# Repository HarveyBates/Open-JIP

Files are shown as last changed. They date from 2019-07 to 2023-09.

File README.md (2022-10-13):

<p align="center">
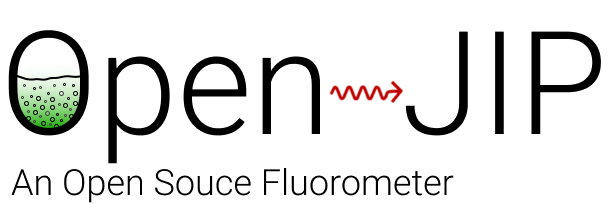
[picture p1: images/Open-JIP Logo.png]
  
</p>

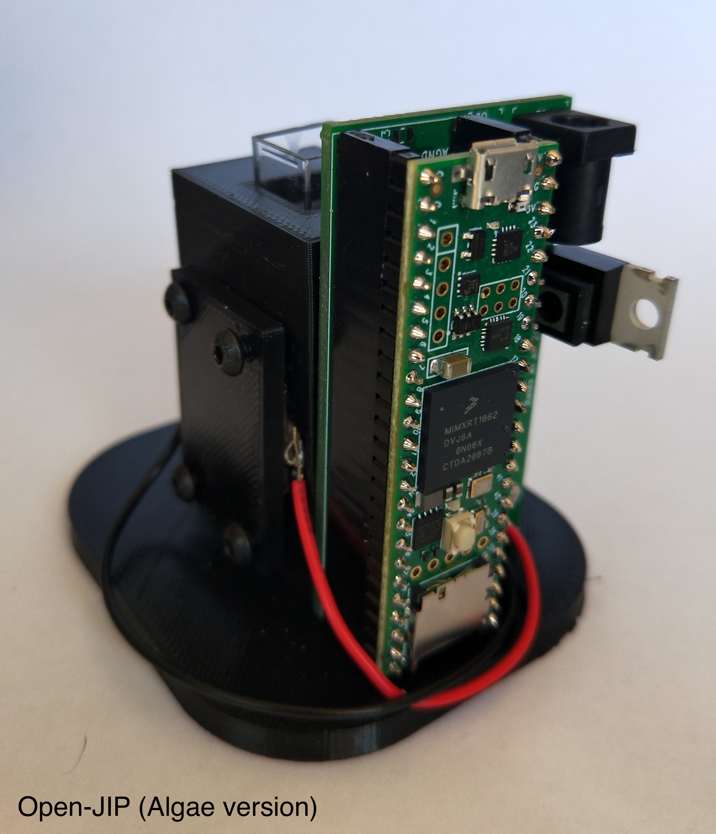
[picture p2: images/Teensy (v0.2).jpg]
### Description

Open-JIP is an open-source chlorophyll *a* fluorometer used to quantify photosynthetic phenotypes in terrestrial plants and microalgae. It is controlled via a Teensy microcontroller and features highly customisable electrical components and a 3D-printed infrastructure. 

#### OJIP

Open-JIP utilises a technique known as the fast polyphasic rise fluorescence
(also known as OJIP). Steady irradiance is provided from an emitting LED, this
excites photosynthetic antenna in the sample resulting in excess irradiance
being emitted as photons of a longer wavelength (i.e. fluorescence). The
emitted fluorescence, which contains information regarding the state of
photosynthesis, is captured by a photodiode, amplified by the custom circuitry
and stored by the Teensy microcontroller. This all happens in less than a second.

The transient captured by Open-JIP gives the user an indication of the state of photosynthesis in the subject organism to varying levels of complexity. If you would like to know more about the theory surrounding the measurement of chlorophyll *a* fluorescence, this [link](https://doi.org/10.1016/j.algal.2020.102105) gives a basic introduction and resources for further reading.

### Publication

The original device which used an Arduino Mega was published in [Photosynthesis Research in 2019](https://doi.org/10.1007/s11120-019-00673-2):

*A guide to Open-JIP, a low-cost open-source chlorophyll fluorometer - Bates et al. 2019*

If you would like to see what the device is capable of, you may be interested in this recent [publication](https://doi.org/10.1016/j.algal.2020.102105) which uses Open-JIP as a flow-through chlorophyll *a* fluorometer connected [a custom photobioreactor](https://github.com/HarveyBates/Phenobottle) with the microalga *Chlorella vulgaris*.

### Collaborations and custom architecture 

If you would like to collaborate on a project, or would like to see if Open-JIP can be customised to suit your application, please email me at [harvey_bates@hotmail.com](mailto:harvey_bates@hotmail.com). 

### Disclaimer

Open-JIP requires some knowledge of electronics, programming and photosynthesis to operate. If you have problems with the device place an issue in the [issues](https://github.com/HarveyBates/Open-JIP/issues) tab of this repository and I will do my best to address it as soon as possible.

# USER MANUAL

Below contains the user manual for Open-JIP, if you have any questions there is a discussions tab in this github repository, where I will do my best to get back to you as soon as possible.

## Contents

1. Introduction
   1. Specifications
   2. Getting started
      1. Downloading files
         1. Method 1 (New users)
         2. Method 2 (Experienced users / collaborators)
      2. Gathering materials
         1. Printed circuit board (PCB)
            1. Ordering a PCB
         2. 3D models
         3. Additonal parts
2. Firmware / Software
   1. Introduction
   2. Arduino IDE / Teensyduino
   3. Basic operations
      1. Basic functions
      2. Advanced functions
      3. Calibration functions
   4. Python control
   5. Advanced operations
      1. Change actinic LED intensity
      2. Change detection sensitivity
      3. Set analog reference voltage & Resolution
      4. Defaults
      5. Length of actinic pulse
3. Hardware
   1. Detection
      1. Gain adjustment 
   2. Actinic Intensity

## 1. Introduction

### Specifications

| Feature            | Value / Description                                          |
| ------------------ | ------------------------------------------------------------ |
| Actinic LED Colors | **Blue** 455 – 485 nm (466 nm), **Green** 517 – 555 nm (532 nm), **Orange** 583 – 600 nm (593 nm), **Red** 617 – 635 nm (626 nm). |
| Resolution         | 10 to 16-bit (optimised for 12-bit)                          |
| Sampling rate      | 8 &mu;s at 12-bits                                           |
| Operating voltage  | 15 V 1.2 A (Barrel plug)                                     |
| Communications     | USB (Serial)                                                 |
| Microcontroller    | Teensy 3.5/3.6 or Teensy 4.1 (3.6 Recommended)               |
| Actinic Intensity  | Four intensities (Low, Mid, High, Very High)                 |
| Detection (Gain)   | Four settings (Low, Mid, High, Very High)                    |

### Getting started

#### Downloading files

##### Method 1 (New users)

New users should navigate to the [releases](https://github.com/HarveyBates/Open-JIP/releases) page to find the most recent (and stable) version of the device. You can download the latest release as a `.zip` file and this will contain all the files you need to get the device up and running. 

The most recent version is **v0.3**. 

When searching through files in this repository all relevant folders are labeled with a specific version. You will want to use files that match the version you are using.

##### Method 2 (Experienced users / collaborators)

If you want to contribute to the project or fork this directory feel free to do so, just know that I constantly update files here so they may not function as expected before release. 

To clone this directory type this into your terminal / console.

```bash
git clone https://github.com/HarveyBates/Open-JIP.git
```

#### Gathering materials

Open-JIP can be built in an afternoon if you have all the equipment at hand. The folder "Bill of Materials" contains all the materials needed to build Open-JIP. This has been divided into two parts; (1) circuit board and (2) other. 

In addition to the Bill of Materials you will need to have access to:

1. A soldering iron
2. Solder (Paste or wire variety)
3. A re-flow oven (not necessary but makes the circuit board easier to assemble)
4. A 3D-printer
5. A pair of wire strippers / cutters
6. Some tweezers

##### Printed circuit board (PCB)

In the ```Bill of Materials/Circuit Board``` folder you will find a table all the components needed to construct the Open-JIP circuit board. These components can be bought from common electronics suppliers such as [digikey](https://www.digikey.com/), [LCSC](https://lcsc.com/en) or [farnell](https://au.element14.com/) etc. Links for each component is provided.

Note that most of the components are surface mount (SMD), this is due to their increased reliability and in my opinion its easier to assemble SMD compared to through-hole (THT) components. 

###### Ordering a PCB

To order the circuit board I recommend using [JLCPCB](https://jlcpcb.com/) as they are cheap, easy and ship fast. 

1. Open the folder titled Electronics 
2. Navigate to your current version 
3. In the subdirectory select the folder containing gerber and drl files
4. Compress this folder into a ```.zip``` file. 
5. On the JLCPCB website drag and drop the ```.zip``` file into the order form. 

The default settings are suitable. 

##### 3D Models

The 3D-models used for 3D-printing Open-JIP can be found in the ```Open-JIP/Hardware``` folder. Two file types are specified:

1. ```.stl``` can be directly imported into 3D-printing software such as [Ultimaker-Cura](https://ultimaker.com/software/ultimaker-cura) or sent to a local 3D-printing manufacturer.
2. ```.STEP``` is the modifiable Open-JIP 3D-model and as such can be configured whichever way you want before being exported as a ```.stl``` file. You can use 3D modeling software to do this such as [Fusion360](https://www.autodesk.com/products/fusion-360/overview) or [Solidworks](https://www.solidworks.com/).

##### Additional parts

In addition to the above electronics you will need a few components such as a Teensy microcontroller, power supply, computer to use the device etc. A table of all these additional items can be found in the folder location ```Bill of Materials/Other```.

## 2. Firmware / Software

### Introduction

Open-JIP operates via a computers serial port (USB connection), the user sends commands in the form of strings that are read by the Teensy microcontroller. This results in the device taking a measurement or other tasks. You can do this manually though the Arduino IDE or by using scripts in various languages. 

### Arduino IDE / Teensyduino

To setup the Teensy (upload the firmware to the microcontroller) you will need **both** [Arduino IDE](https://www.arduino.cc/en/software) and [TeensyDuino](https://www.pjrc.com/teensy/teensyduino.html) if running on Linux or Windows, or just [TeensyDuino](https://www.pjrc.com/teensy/teensyduino.html) if using a Mac. Instructions on how to do this is provided in the above links. 

When first using Open-JIP: 

1. Plug the Teensy into your computer
2. Open Arduino IDE
3. Select ```Tools>Board>Teensy 3.6``` (may be in another part called Teensyduino)
4. Select ```Port>"Your Teensy Device"```
5. ```File>Open``` the "Teensy.ino" file found in ```Firmware/v0.3/Teensy_3.6/Teensy_3.6.ino```
6. ```Sketch>Upload``` to flash the file onto the Teensy

The provided ```Teensy.ino``` file will work as is, but if you wish to change settings in this file you will need to reupload the firmware to the Teensy again after changes have been made.

### Basic Operations

To take a measurement open the serial monitor (in the Arduino IDE when the device is connected to your computer) (```Tools>Serial Monitor```) and type in the command ```MF``` (denoting **m**easure **f**luorescence). This will (in the default configuration) take a one second measurement of chlorophyll *a* fluorescence and print the resulting measurements out into the serial monitor. You can copy and paste the data into excel in order to graph the transient.

There are a number of included functions that require the same method to operate:

#### Basic functions

1. ```MF``` - **M**easure fluorescence. Measure the chlorophyll *a* fluorescence signature of the organism of interest. 
2. ```CP``` - **C**alculate **p**arameters. Calculate and print out basic fluorescence parameters from the most recent OJIP curve. 
3. ```CFo``` - **C**alibrate **F<sub>o</sub>** (the minimum level fluoresence). Provides short flashes of illumination for calibrating the minimum level fluorescence. This command is useful if you want to know if your measurement is going to *saturate* (due to an overly concentrated sample) before taking a measurement. 
4. ```An``` - **A**ctinic intensity (irradiance of LED) where *n* is a number between 1 and 4 (lowest to highest).
5. ```Fn``` - **F**luorescence gain (sensitivity of detection) where *n* is a number between 1 and 4 (lowest to highest).

**Note** - It is recommended that the minimum level of fluorescence (F<sub>o</sub>) is greater than 0.3 V for the maximum stability of acquisitions.

#### Advanced functions

1. ```MJ``` - **M**easure **J**-step. Measures up to the J-step (~2 ms) and returns the data to the serial port.
2. ```MW``` - **M**easure **w**ave. Measures up to the J-step multiple times with set time intervals between acquisitions. 

#### Calibration functions

1. ```ML``` - Calibrate actinic intensity (**m**easure **l**ight). Turns on the actinic LED for a period of three seconds to allow the intensity to be measured by a 4&#960; light meter.
2. ```Cr``` **C**alibrate **r**ise time of the actinic LED/amplifier combination. Provides some short  (100us) flashes of illumination from the actinic LED to calibrate your setup using an external oscilloscope. Useful if you want to ensure your Fo value is accurate (i.e. Fo should be measured when the actinic LED and amplifier are stable (usually around 40us)). *Note* this is only nessesary if you alter the default electronics configuration (see below).  

### Python Control

Open-JIP comes with an external cross platform python script that allows users to take basic measurements, plot the data and sort it into a ```.csv``` file automatically. This program is located under ```External Control/Open-JIP.py```.

```Open-JIP.py``` uses [plotly](https://plotly.com/python/) to plot the data and [pyserial](https://pyserial.readthedocs.io/en/latest/pyserial.html) to access the serial port of your machine. You must have [python](https://www.python.org/) installed to use this script. **This program runs in the terminal / console**. Additonally you need pip to install these requirements as follows:

```bash
cd Open-JIP/Software
pip3 install -r requirements.txt
python3 Open-JIP.py
# or (depending on python installation)
pip install -r requirements.txt
python Open-JIP.py
```

If you wish to change the output path of the ```.csv``` file you can do so by changing this string in ```Open-JIP.py```:

```python
fileName = "Open-JIP_Data.csv"  # Filename of output .csv file
```

### Advanced operations

A major feature of Open-JIP is its customisability. In the firmware users can adjust:

1. The actinic LED intensity
2. The detection sensitivity
3. The analog reference voltage
4. Resolution of the device
5. Length of actinic pulse

This next section is going to be in reference to the files located within ```Firmware/v0.3/Teensy_3.6```.

#### Change actinic LED intensity

In ```actinic.cpp``` the actinic LED intensity can be adjusted. There are four possible configurations, LOW, MID, HIGH, VERY HIGH. These can be selected by applying the values 1 - 4 (LOW - VERY HIGH) when switching on the actinic LED. 

```C++
void Actinic::on(){
  switch(intensity){
    case 1:
      digitalWrite(actinicGain1, HIGH); // Low
    	break;
    case 2:
      digitalWrite(actinicGain2, HIGH); // Mid
      break;
    case 3:
      digitalWrite(actinicGain3, HIGH); // High
      break;
    case 4:
      digitalWrite(actinicGain4, HIGH); // Very high
      break;
  }
}
```

*Note-* Electrical components have intrinsic variability. If using identical devices ensure actinic intensity is similar using a PAR meter.

*DO NOT -* combine actinic LED intensities as this will result in undefined behaviour. 

#### Change detection sensitivity

In ```sensitivity.cpp``` the detection sensitivity can be adjusted. There are four possible detection configurations, LOW, MID, HIGH, VERY HIGH (1 - 4). These are set before starting an exposure for stability and are therefore defined by the user.

```C++
void Sensitivity::define(int _gain){
    refresh();
    switch(_gain){
        case 1:
            // Lowest
            digitalWrite(fluoroGain1, HIGH); // Photosynthesis (OJIP)
            break;
        case 2:
            digitalWrite(fluoroGain2, HIGH); // Photosynthesis (OJIP)
            break;
        case 3:
            digitalWrite(fluoroGain3, HIGH); // Concentration only (not recommended for photosynthesis)
            break;
        case 4:
            // Highest
            digitalWrite(fluoroGain4, HIGH); // Concentration only (not recommended for photosynthesis)
            break;
    }
}
```
**NOTE**

Recent testing of the gain settings of Open-JIP has led to the conclusion that the current version of the device (v0.3) can only use gain 1 and 2 for photosynthesis (OJIP) measurements. Gain 3 and 4 should only be used for concentration estimates using the fluorescence intensity at ~120 &mu;s.

 *DO NOT* - combine gain settings as this will result in undefined behaviour. 

#### Set analog reference voltage & Resolution

In ```fluorescence.cpp``` the reference voltage can be adjusted to either 3.3 or 1.1 volts when using a Teensy 3.6. The purpose of this is (1) the Teensy 3.6 (1.1 V) reference voltage is more stable than 3.3 V and (2) you can attain a higher resolution when measuring weak fluorescence signals.

```C++
void Fluorescence::set_reference_voltage(float voltage){
  // Sets and initialises the required reference voltage for measurements
  if(voltage == 3.3){
    analogReference(DEFAULT); // Set to 3.3 V
  }
  else if(voltage == 1.1){
    analogReference(INTERNAL1V1); // Set to 1.1 V
  }
  else{
    analogReference(DEFAULT); // Set to default (3.3 V) if unknown value is found
  }
  analogRead(readPin); // Initialise reference voltage
}
```

*Note* - This is usually done statically at the start of the program by adjusting the value of ```refVoltage``` to either 3.3 or 1.1 depending on your requirements.

The number of bits for each reading can be changed via this command in the ```void setup()``` function:

```c++
analogResolution(12); // 12-bit resolution
```

*Note* - **Increasing** the resolution **decreases** the sampling rate so if you want to get alot of data points around Fo I reccomend you use a 12 or 10-bit resolution.

If you use have a 12 bit-resolution with a reference voltage of 1.1V the finest sensivitiy of the device is 0.00027 V per-division (1.1V / 2<sup>12</sup>) at a 8 &mu;s sampling rate. 

#### Defaults

Upon startup, Open-JIP will revert to its default configuration. You can change this by altering the setup command in ```Teensy_3.6.ino```:

```C++
void setup() {
  Serial.begin(115200); // Starting baud rate
  analogReadResolution(12); // Default resolution
  pinMode(13, OUTPUT); // Sets the microcontrollers LED pin as an output
  
  sensitivity.refresh(); // Switch off all sensitivity settings
  sensitivity.define(1); // Set a default sensitivity (1 - 4)

  actinic.off(); // Switch off all actinic settings
  actinic.define(1); // Set a default actinic irradiance (1 - 4)
}
```

#### Length of actinic pulse

In ```fluorescence.h``` the length of the actinic exposure (pulse) can be adjusted. The acquisition is done in two steps; (1) the fast measurments (readings every 8 &mu;s) and (2) slow (readings every 1 ms). These arrays require different processing methods and are therefore stored seperately. Below gives you an idea of how the array lengths are calculated for the intial aqusitions and the converted output. 

```c++
// Microsecond (micro) = readings every 8 us
static const unsigned int microLength = 1000; 
int microRead [microLength];
int milliRead[microLength];

// Millisecond (milli) = readings every 1 ms
static const unsigned int milliLength = 1000; 
int microTime[milliLength]; 
int milliTime[milliLength];

// Stores final array in converted form (i.e. Volts and Milliseconds)
float fluorescenceValues[microLength + milliLength];
float timeStamps[microLength + milliLength];
```

*Note* - If you are using the ```Open-JIP.py``` script you will need to change the number of data points that are read to match the length of ```fluorescenceValues```:

```python
timeStamps, fluorescenceValues = measure_fluorescence(2000) # Match with teensy script array length (default 2000)
```

## 3. Hardware

Open-JIP operates using a Teensy 3.6 microcontroller connected to a custom printed circuit board (PCB). The circuit is divided into two parts:

1. Detection - Responsible for detecting emitted fluorescence
2. Actinic intensity - Responsible for turning on and off the actinic LED

### Detection

Fluorescence detection is achieved with the use of an operational amplifier (op-amp) connected as a transimpedance amplifier. The inverting input is connected to a photodiode, while the non-inverting input is connected to a voltage divider to provide a very small offset voltage. The concept of the offset voltage is that the amplifier (op-amp) will respond faster to changes in voltage. 

*Note-* Resistor values may change depending on your application.

<p align="center">
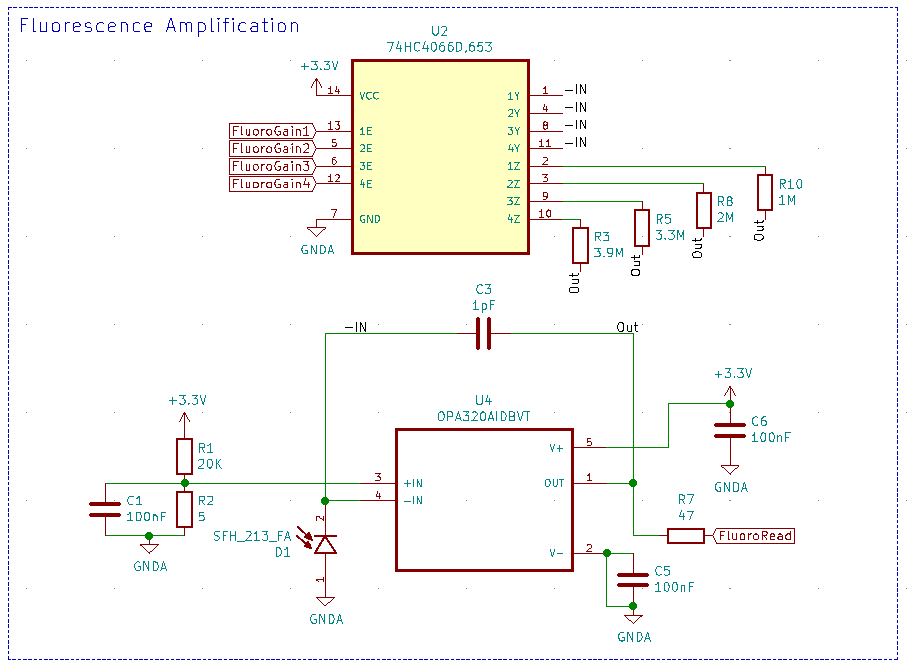
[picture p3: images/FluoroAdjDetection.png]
  
</p>

#### Gain adjustment

Four different sensitivities are provided though the use of a CMOS switch (74HC4066D) which has a range of different feedback resistors (1M, 2M, 3.3M and 3.9M). These resistors are all 0805 SMD. The gain is selected in the firmware of Open-JIP; however, if you wish to adjust the senstivity futher you can do so by changing one or more of these resistors. 

**Increasing** the resistance of the feedback resistor will **increase** the sensitivty of detection.

**Decreasing** the resistance of the feedback resistor will **decrese** the sensitivty of detection.

**Note**

Feedback resistances above 2Mohm are not suitable for OJIP measurements in v0.3. Ideally the feedback resistor should be a small as possible to increase the response time of the device.

**Note**

If you begin to get a large overshoot occurring at the start of your measurements you may need to increase the capacitor value (C3) to 2pF - 5pF. This [article](https://wiki.analog.com/university/courses/electronics/electronics-lab-1st) may help you if you encounter this issue.

### Actinic intensity

The actinic LED is controlled in the same way as the detection circuit i.e. Using a CMOS switch to controll its brightness. Again four levels of brightness can be selected in the firmware and are controlled by resistors (10K, 12K, 15K, 20k) connected to the base of the darlington transisitor (BD681). Adjusting the value of these resistors will result in the LED getting brighter or dimmer based on their resistance value.

*Note-* Resistor values may change depending on your application.

<p align="center">
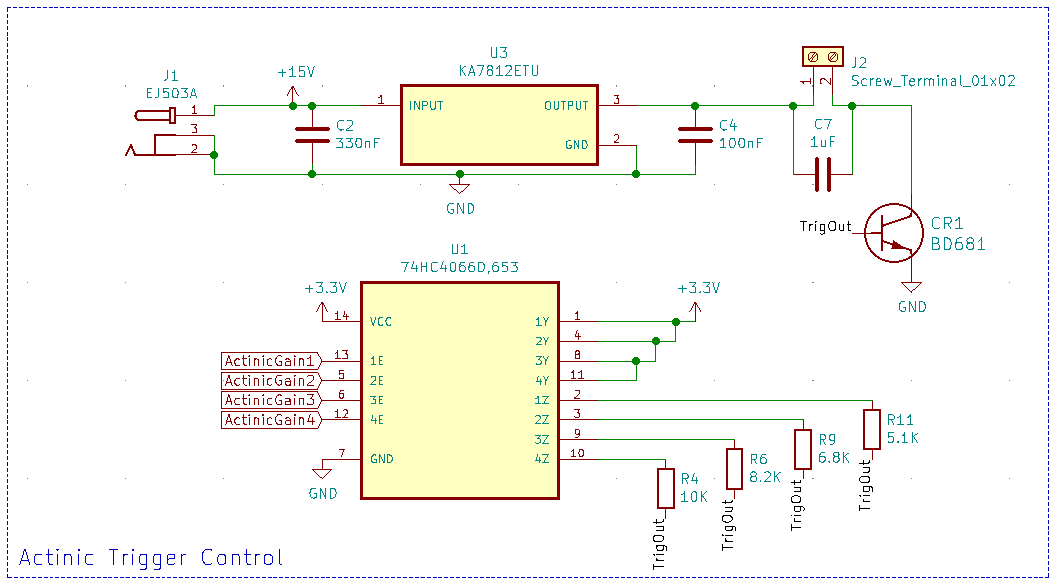
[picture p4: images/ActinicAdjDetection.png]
  
</p>

The input voltage (15 V) is filtered through a 12 V linear voltage regulator. This regulator ensures the actinic LED is stable of the measurement. A small capacitor (C7 - 1 &mu;F) is placed across the LED's terminal to prevent overshoot. If you want the LED to respond faster you can reduce the value of this capacitor while using an oscilloscope to check the devices rise-time. 

**Increasing** the resistors results in **decreased** actinic brightness.

**Decreasing** the resistance of R10 results in **increased** actinic brightness.

**Note**

Gate resistor values are dependent on a number of factors including manufacturer tolerances and LED color. Dialing in the resistor values to use in your device is an important consideration. Typically you will need a PAR meter to calibrate the devices brightness before use (if using for OJIP measurements). However, if access to a PAR meter is an issue, the shape of the OJIP curve can be an indicator of LED intensity. If the rise between Fo and Fj is sharp and rapid (<2ms), typically the device has enough brightness to saturate the electron transport chain. However, if the rise between Fo and Fj is gradual (>2ms), the brightness may not be bright enough. 

## Future of Open-JIP

Since the publication of Open-JIP a number of changes have been made to increase the devices capabilities. These include:

1. ~~Adjustable fluorescence protocols~~

2. ~~Ability to change detection sensitivity dynamically (though software)~~

3. ~~Adjustment of actinic LED intensity dynamically (through software)~~
4. Improvements in resolution
5. Improvements in number of datapoints in each OJIP transient

## Licence

The software in this work is licensed under GNU AFFERO GENERAL PUBLIC LICENSE Copyright (C) (2020) (Harvey Bates)

This program is free software: you can redistribute it and/or modify it under the terms of the GNU General Public License as published by the Free Software Foundation, either version 3 of the License, or (at your option) any later version.

This program is distributed in the hope that it will be useful, but WITHOUT ANY WARRANTY; without even the implied warranty of MERCHANTABILITY or FITNESS FOR A PARTICULAR PURPOSE. See the GNU General Public License for more details.

You should have received a copy of the GNU General Public License along with this program. If not, see https://www.gnu.org/licenses/

For more information contact: [harvey_bates@hotmail.com](mailto:harvey_bates@hotmail.com)



The hardware (3D Models, Electronic Schematics) in this work is licensed under a [Creative Commons Attribution-ShareAlike 3.0 Unported License](http://creativecommons.org/licenses/by-sa/3.0/).

[https://doi.org/10.1016/j.algal.2020.102105]: 
[https://pyserial.readthedocs.io/en/latest/pyserial.html]:

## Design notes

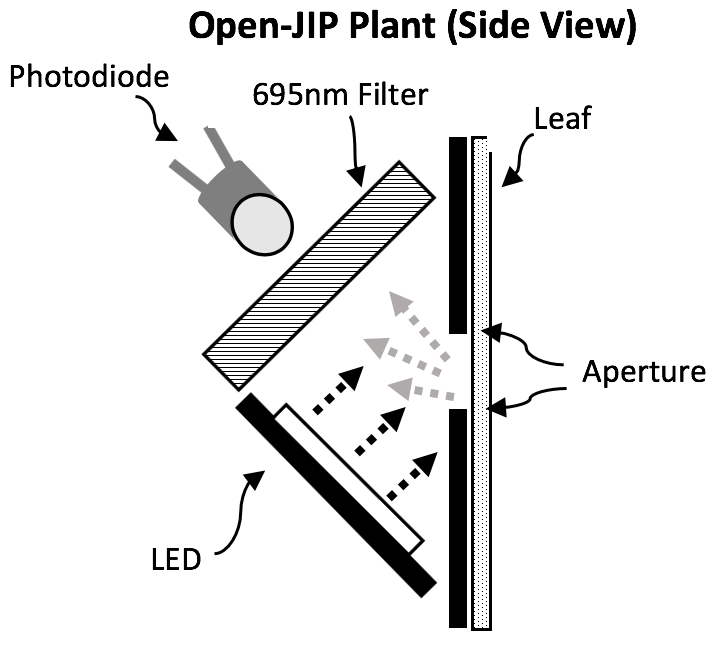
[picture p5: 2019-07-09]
images/Open-JIP Plant Diagram.png

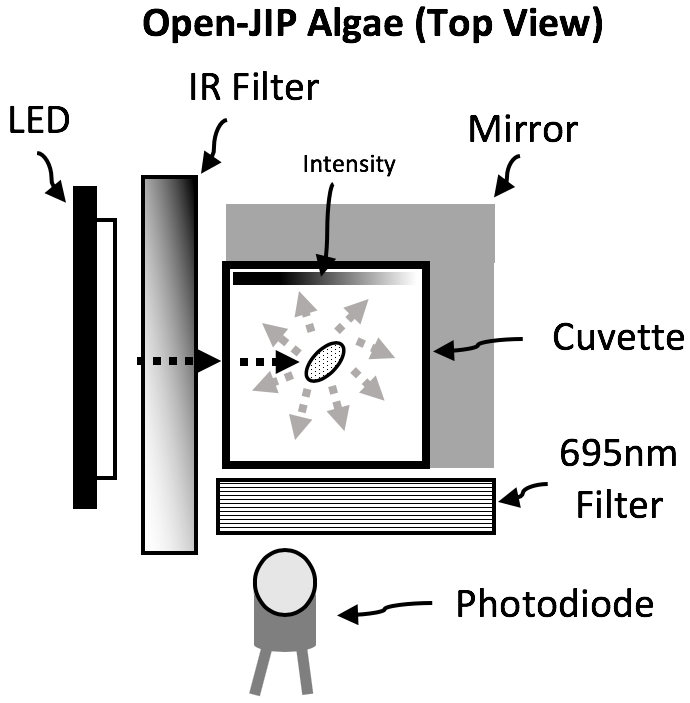
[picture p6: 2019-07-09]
images/Open-JIP Algae Diagram.png

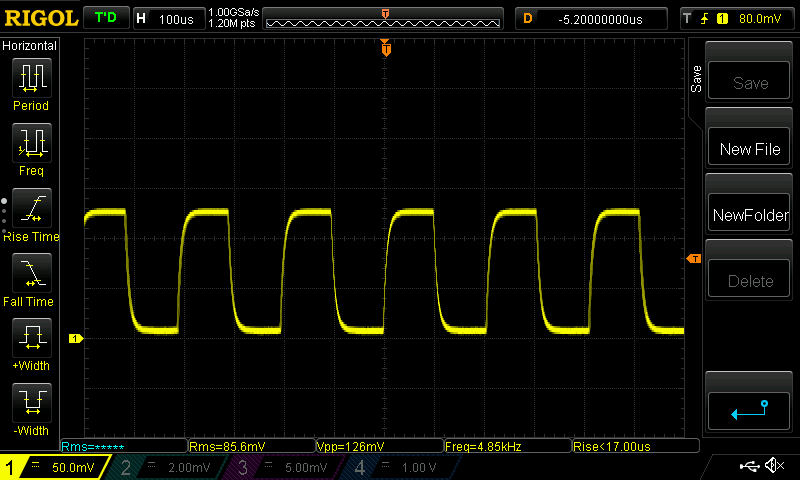
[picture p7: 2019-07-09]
images/Detection_Rise-time.png

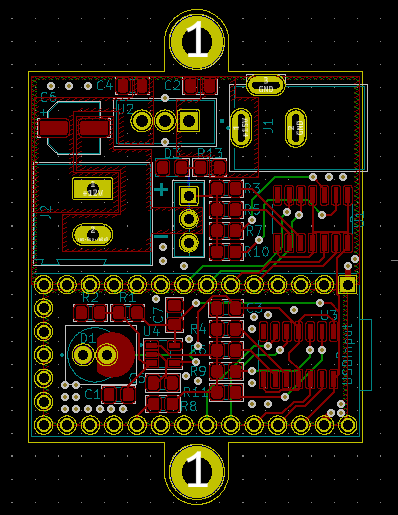
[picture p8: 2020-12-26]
images/Teensy3.2_Open-JIPv0.3.png

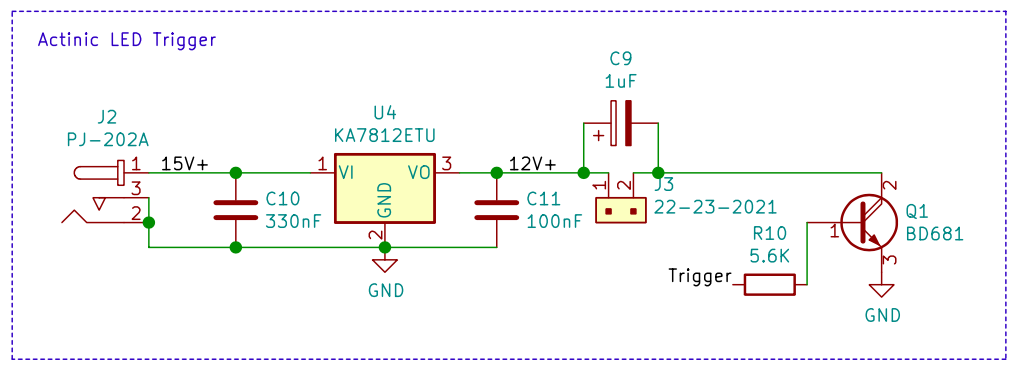
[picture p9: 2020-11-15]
images/ActinicCircuit.png

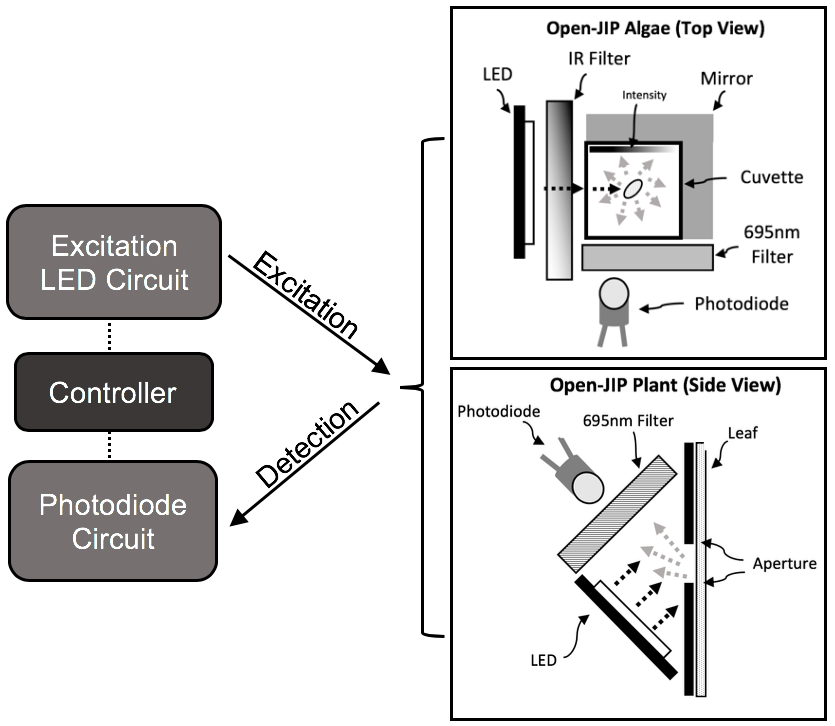
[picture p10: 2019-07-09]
images/Open-JIP Diagram.png

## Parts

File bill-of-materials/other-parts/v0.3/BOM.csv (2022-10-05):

Item | Quantity | Required | Notes | Website
Teensy 3.5/3.6 or 4.1 | 1 | Y | Can get 3.5, 3.6 or 4.1 (3.6 recommended), if getting Teensy without pins you will need to get 2.54mm two male headers (1x24 pins) | https://www.pjrc.com/store/teensy36.html
3D-Printed MainFrame | 1 | Y | Main structure, holds cuvette (modify for flow-through configuration) | See repository
3D-Printed LEDCover | 1 | Y | Holds the LED in-place | See repository
3D-Printed Lid | 1 | Y | Covers the cuvette for dark-adaptation
Power supply (15DYS818-150120W-K) | 1 | Y | 15 V 1.2 A Power Supply (ensure you use 15V or greater) | https://cpc.farnell.com/ideal-power/15dys618-150120w-k/ac-dc-power-supply-15v-1-2a-intl/dp/PW04156
MicroUSB to USB Adaptor | 1 | Y | Any one will do
22.6x30x3mm Plexiglass (Acrylic) Mirrored | 1 | Y | Used to surround the cuvette and increase the change of photons hitting the detector (breath x height x width) | Any plexiglass supplier
16.6x30x3mm Plexiglass (Acrylic) Mirrored | 1 | Y | Used to surround the cuvette and increase the change of photons hitting the detector (breath x height x width) | Any plexiglass supplier
Cuvette (Polystyrene) | 1 | Y | Or glass | https://www.sigmaaldrich.com/catalog/product/sigma/c0918?lang=en&region=AU
25mm IR Filter | 1 | N | Optional filter if you are getting interference from the actinic LED
ND Filter | 1 | N | Optional any ND filter paper will do or use a 25mm ND filter in front of the actinic LED
16 AWG Wire (Red and Black) | 1 ea | Y | For attaching LED to circuit board | https://www.ebay.com.au/p/2119056858
10W COB LED | 1 | Y | Suppliers change for this LED, but look for 10W COB LED (Red, Green, Blue) on ebay and you will find them | https://www.ebay.com.au/itm/10W-20W-30W-50W-70W-100W-12V-36V-High-Power-LED-Lamp-Light-COB-SMD-Bulb-Chip-DIY/323902290356
Threaded Inserts (M3) | 4 | Y | For attaching LED cover to 3D-printed frame
M3 12mm Bolt (x 4) | 4 | Y | For attaching LED cover to 3D-printed frame

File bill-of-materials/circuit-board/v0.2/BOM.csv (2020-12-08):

Value | Designator (Location) | Quantity | Footprint | Required | Notes | Website
330nF | C10 | 1 | Capacitor_SMD:C_0805_2012Metric | Y | Capacitor SMD | https://lcsc.com/product-detail/Multilayer-Ceramic-Capacitors-MLCC-SMD-SMT_FH-Guangdong-Fenghua-Advanced-Tech-0805B334K500NT_C1740.html
1pF | C5 | 1 | Capacitor_SMD:C_0805_2012Metric | Y | Capacitor SMD | https://lcsc.com/product-detail/Multilayer-Ceramic-Capacitors-MLCC-SMD-SMT_Walsin-Tech-Corp-0805N1R0C500CT_C424847.html
100nF | C6,C7,C8,C11 | 4 | Capacitor_SMD:C_0805_2012Metric | Y | Capacitor SMD | https://lcsc.com/product-detail/Multilayer-Ceramic-Capacitors-MLCC-SMD-SMT_TORCH-CT41G-0805-2X1-50V-0-1mF-M-N_C138340.html
1uF | C9 | 1 | Capacitor_SMD:CP_Elec_ 4x5.4mm | Y | Capacitor Electrolytic 4 x 5.4mm | https://lcsc.com/product-detail/Aluminum-Electrolytic-Capacitors-SMD_ST-Semtech-CS1H010M-CRC54_C116391.html
PJ-202A | J2 | 1 | Barrel_Jack_5.5mmODx2.1mmID_PJ-202A | Y | Barrel Jack for 15 V 1.2 A power supply | https://lcsc.com/product-detail/AC-DC-Power-Plugs-Receptacles_GANGYUAN-DC-470-2-1GP_C194407.html
SFH_213 | PV1 | 1 | Photodiode_5mm_Radial_IR_Filtered | Y | Photodiode (IR Filtered) | https://au.element14.com/osram-opto-semiconductors/sfh213-fa/photodiode-ir-filtered/dp/1212763?st=SFH213-FA
BD681 | Q1 | 1 | BD681_Darlington_Transistor | Y | Transistor (Darlington) | https://lcsc.com/product-detail/Darlington-Transistors_STMicroelectronics-BD681_C703688.html
5.6K | R10 | 1 | Resistor_SMD:R_0805_2012Metric | Y | Resistor, May want a range (3K – 15K) | https://lcsc.com/product-detail/Chip-Resistor-Surface-Mount_5-6KR-562-5_C159921.html
4.7M | R5 | 1 | Resistor_SMD:R_0805_2012Metric | Y | Resistor, May want a range (3.3M to 10M) | https://lcsc.com/product-detail/Chip-Resistor-Surface-Mount_HKR-Hong-Kong-Resistors-RCT054M7FLF_C185697.html
47 | R6 | 1 | Resistor_SMD:R_0805_2012Metric | Y | Resistor | https://lcsc.com/product-detail/Chip-Resistor-Surface-Mount_Walsin-Tech-Corp-WR08X470JTL_C168501.html
20K | R7 | 1 | Resistor_SMD:R_0805_2012Metric | Y | Resistor | https://lcsc.com/product-detail/Chip-Resistor-Surface-Mount_FH-Guangdong-Fenghua-Advanced-Tech-RS-05K203JT_C139905.html
5 | R8 | 1 | Resistor_SMD:R_0805_2012Metric | Y | Resistor | https://lcsc.com/product-detail/Chip-Resistor-Surface-Mount_FH-Guangdong-Fenghua-Advanced-Tech-RS-05L5R10FT_C304869.html
Teensy3.6 | U2 | 1 | Teensy:Teensy35_36 | Y | Only need one | https://www.pjrc.com/store/teensy36.html
OPA320AIDBVT | U3 | 1 | OPA320AIDBVT:SOT95P280X145-5N | Y | Operational amplifier for detection | https://www.digikey.com/en/products/detail/texas-instruments/OPA320AIDBVT/2751273
KA7812ETU | U4 | 1 | KA7812:TO220V | Y | Linear voltage regulator | https://lcsc.com/product-detail/Dropout-Regulators-LDO_FeiHong-KA7812B_C438618.html
Teensy-Board24Pin | Goes in J3 | 2 | 24 Pin Female Headers x2 | Y | For attaching teeny to circuit board, these are hard to find | https://www.ebay.com.au/itm/2-54mm-Pitch-Female-Pin-Header-Socket-Connector-Strip-2-3-4-5-6-7-40P-Single-Row/264208648021?frcectupt=true

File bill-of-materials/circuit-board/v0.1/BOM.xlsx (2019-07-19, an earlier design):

ID | Name | Designator | Footprint | Quantity | Manufacturer Part | Manufacturer | Supplier | Supplier Part
1 | ARDUINO MEGA 2560 REV3 | U7 | ARDUINO MEGA 2560 REV3 SHIELD | 1 | Arduino
2 | Rf (2.3Mohm) | R1 | AXIAL-0.3 | 1 | ?
3 | 2Kohm | R4 | AXIAL-0.3 | 1 | ?
4 | 1ohm | R6 | AXIAL-0.3 | 1 | ?
5 | Cf (1pF) | C1 | RAD-0.1 | 1 | ?
6 | BPW34R | D1 | PHOTODIODE | 1 | ?
7 | 0.1uF | C3 | RAD-0.1 | 1 | ?
8 | Battery 1 (LiPo 2400mAh) | P1 | HDR-1X2/2.54 | 1 | Generic
9 | Boost Converter | U3 | BOOST CONVERTER CONNECTOR PCB | 1 | DF Robot
10 | IRLZ44NPBF | Q1 | TO-220(TO-220-3) | 1 | IRLZ44NPBF | IR | LCSC | C38774
11 | 2.3Kohm | R5 | AXIAL-0.3 | 1 | ?
12 | ExcitLED | LED1 | LED-5MM/2.54 | 1 | 5AR2ST10 | EVERLIGHT | LCSC | C52721
13 | BD681 | T1 | ONSC-TO-225-3-77-09 | 1 | ?
14 | DC Power (Barrel Plug) | U2 | DC POWER CONNECTOR 2.1MM | 1 | 163-179PH-EX |  | Mouser | 163-179PH-EX
15 | LM358AP | U4 | DIP-8 | 1 | LM358AP | Texas Instruments | LCSC | C163528
16 | LED-5MM | LED2,LED3 | LED-5MM/2.54 | 2 | 5AR2ST10 | EVERLIGHT | LCSC | C52721
17 | 470ohm | R2 | AXIAL-0.3 | 1 | ?
18 | Br (5.6ohm) | R3 | AXIAL-0.6 | 1 | ?
19 | 220ohm | R7 | AXIAL-0.3 | 1 | ?
20 | 1uF | C2 | CAP-D5.0XF2.0 | 1 | ?
21 | KA7812ETU | U1,U5 | TO-220(TO-220-3) | 2 | KA7812ETU | FAIRCHILD | LCSC | C112227
22 | OLED 128x32 (Screen) | U6 | OLED 128X32 | 1
23 | 1825910-2 (Switch) | SW1,SW2 | KEY-6.0*6.0-2 | 2 | 1825910-2 | TE Connectivity | LCSC | C266204

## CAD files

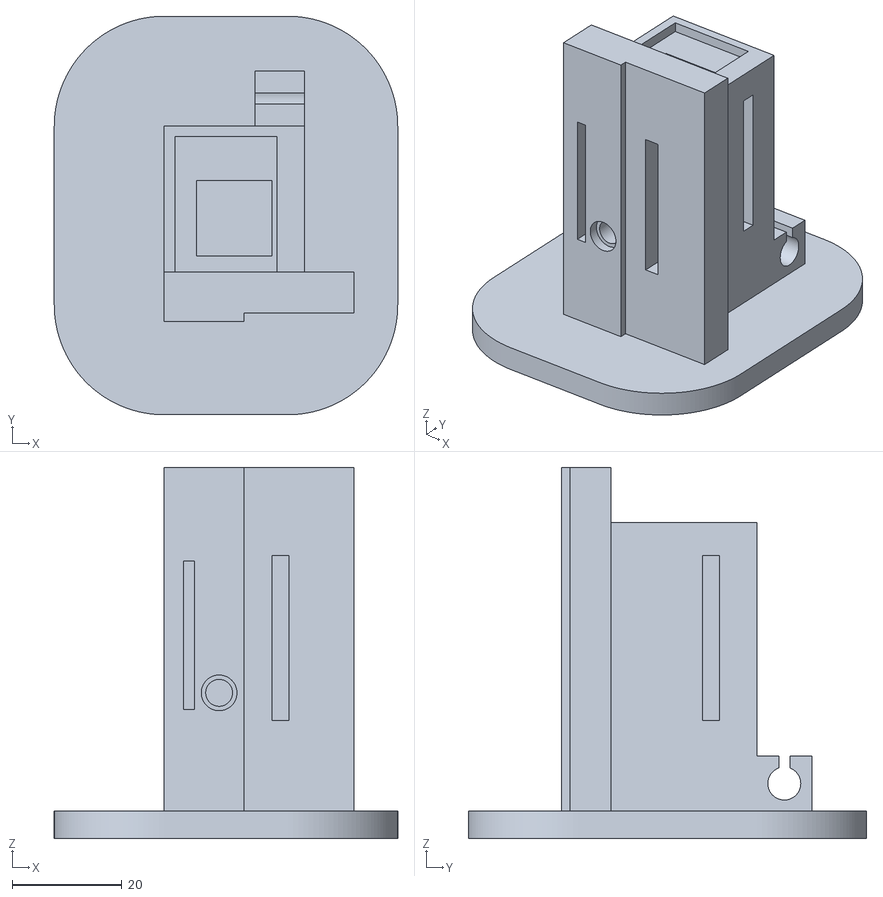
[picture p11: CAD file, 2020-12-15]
hardware/other-files/v0.3/MainFrame.stl
62.5 x 72.5 x 67.5

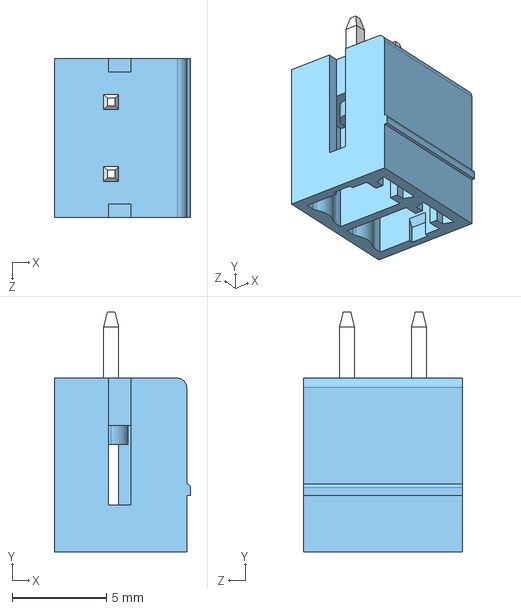
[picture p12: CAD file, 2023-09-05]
electronics/detect/components/extern/3dmodels/connectors/TBP02R2-381-02BE.step
7.20 x 12.7 x 8.41 mm

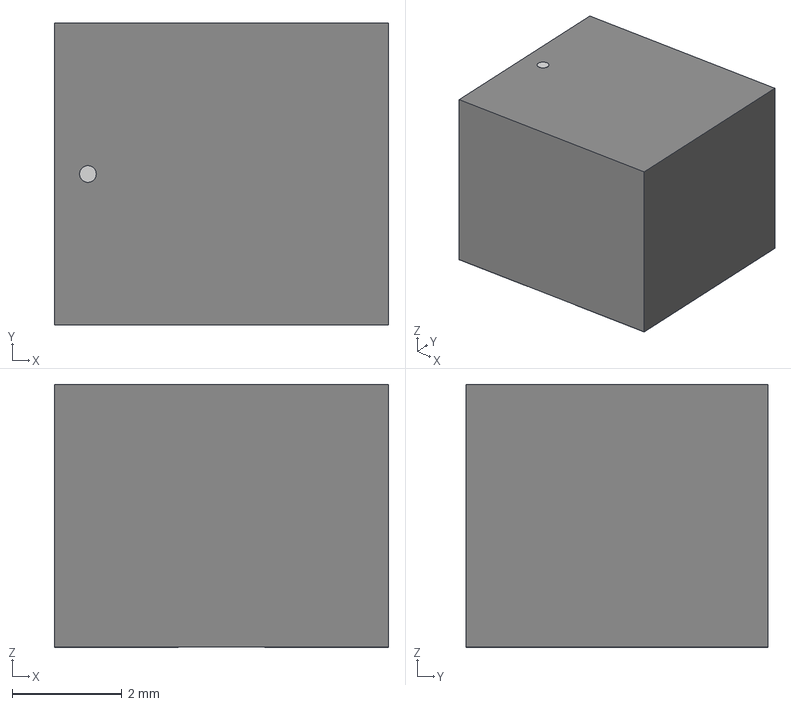
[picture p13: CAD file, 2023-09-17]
electronics/detect/components/extern/3dmodels/inductors/SDE0604A-3R9M.step
6.10 x 5.51 x 4.80 mm

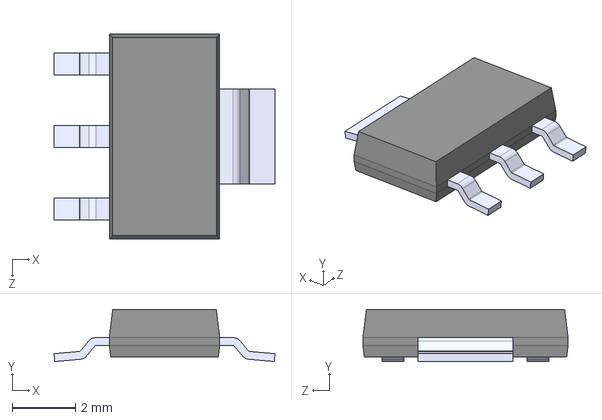
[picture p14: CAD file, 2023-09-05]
electronics/detect/components/extern/3dmodels/mosfets/DMP6023LE-13.step
7.00 x 1.65 x 6.50 mm

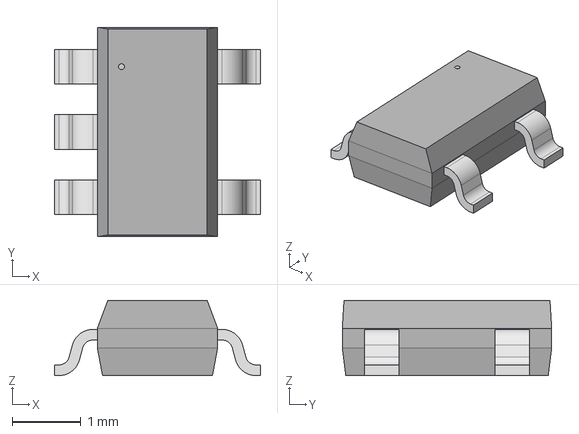
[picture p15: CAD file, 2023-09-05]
electronics/detect/components/extern/3dmodels/op_amps/OPA328DBVR.step
3.00 x 3.05 x 1.09 mm

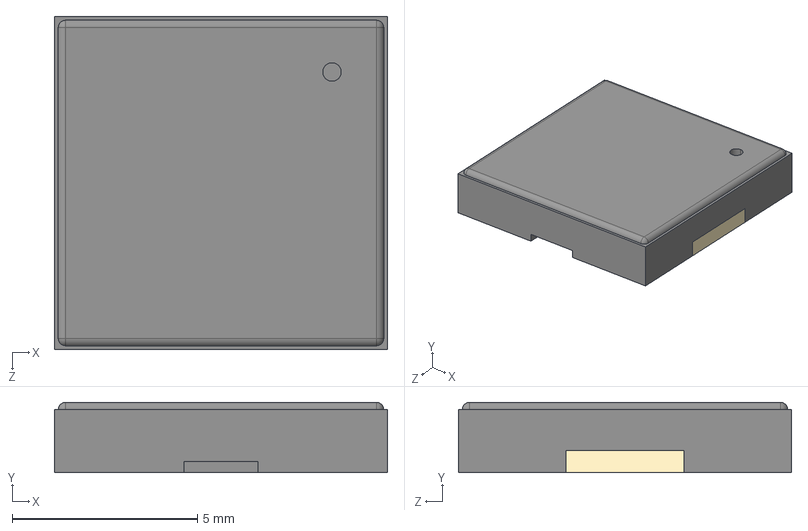
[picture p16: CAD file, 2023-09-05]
electronics/detect/components/extern/3dmodels/piezo/PKMCS0909E4000-R1.step
9.00 x 1.90 x 9.00 mm

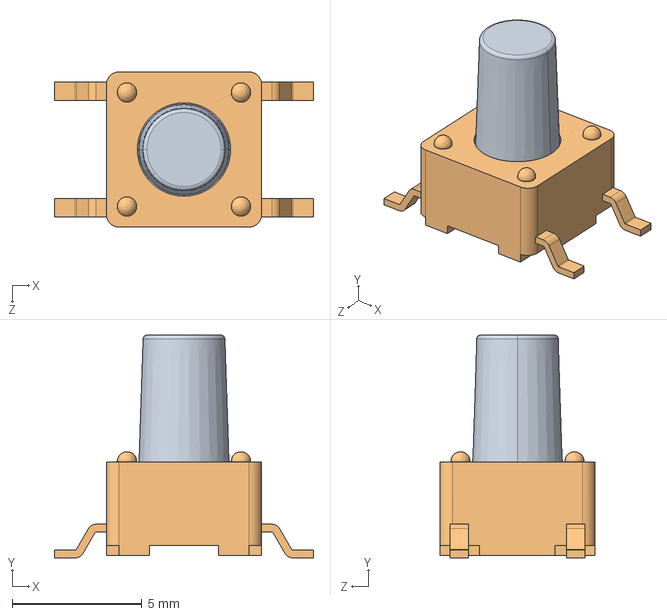
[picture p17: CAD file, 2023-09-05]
electronics/detect/components/extern/3dmodels/switch_tactile/TL3301PF160QG.STEP
10.0 x 8.60 x 6.00 mm

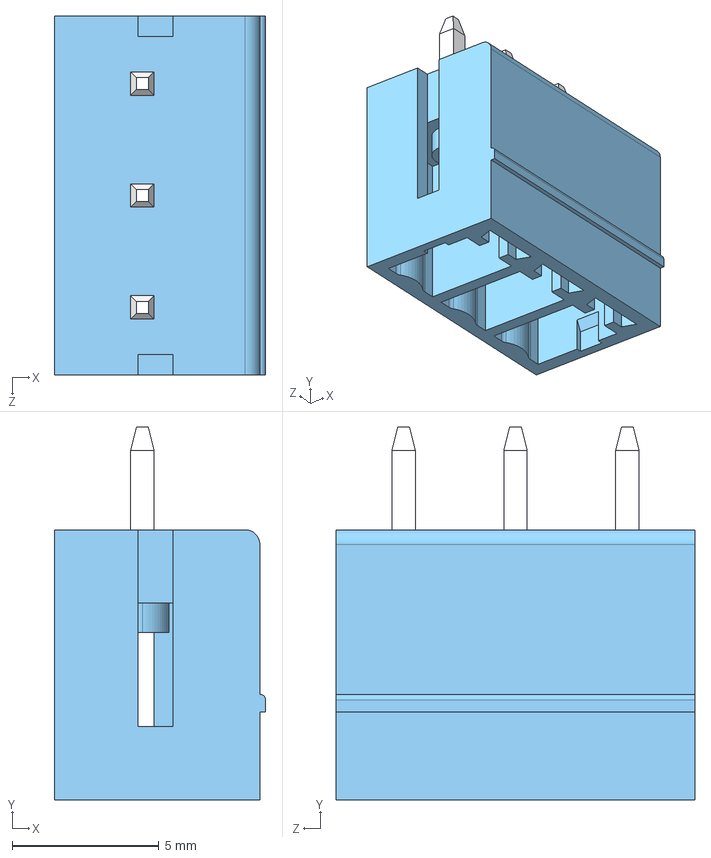
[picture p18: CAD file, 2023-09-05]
electronics/excite/components/extern/3dmodels/connectors/TBP02R2-381-03BE.step
7.20 x 12.7 x 12.2 mm

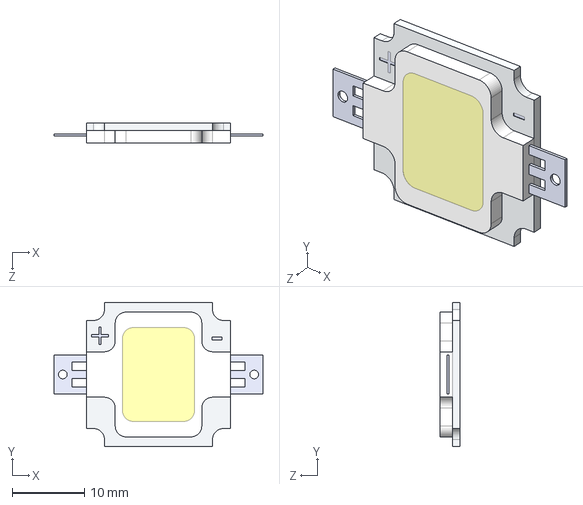
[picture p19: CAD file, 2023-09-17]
electronics/excite/components/extern/3dmodels/leds/10W LED.STEP
29.0 x 20.0 x 2.75 mm

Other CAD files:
electronics/detect/components/extern/3dmodels/connectors/TBP02R2-381-04BE.step
electronics/detect/components/extern/3dmodels/fuses/0154010.DRL.step
electronics/detect/components/extern/3dmodels/ldo/ADP122AUJZ-3.3-R7.step
electronics/detect/components/extern/3dmodels/ldo/AP63205WU-7.step
electronics/detect/components/extern/3dmodels/ldo/MIC29150-12WU.step
electronics/detect/components/extern/3dmodels/ldo/MIC29300-5.0WU-TR.step
electronics/detect/components/extern/3dmodels/switch_tactile/TL3301AF160QG.step
electronics/excite/components/extern/3dmodels/connectors/TBP02R2-381-04BE.step
electronics/excite/components/extern/3dmodels/fuses/0154010.DRL.step
electronics/excite/components/extern/3dmodels/ldo/ADP122AUJZ-3.3-R7.step
electronics/excite/components/extern/3dmodels/ldo/AP63205WU-7.step
electronics/excite/components/extern/3dmodels/ldo/MIC29150-12WU.step
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

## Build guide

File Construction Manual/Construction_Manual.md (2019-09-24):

# Construction of Open-JIP (Electronics)
Below contains an instruction manual for building Open-JIP (Algae).

<p align="center">
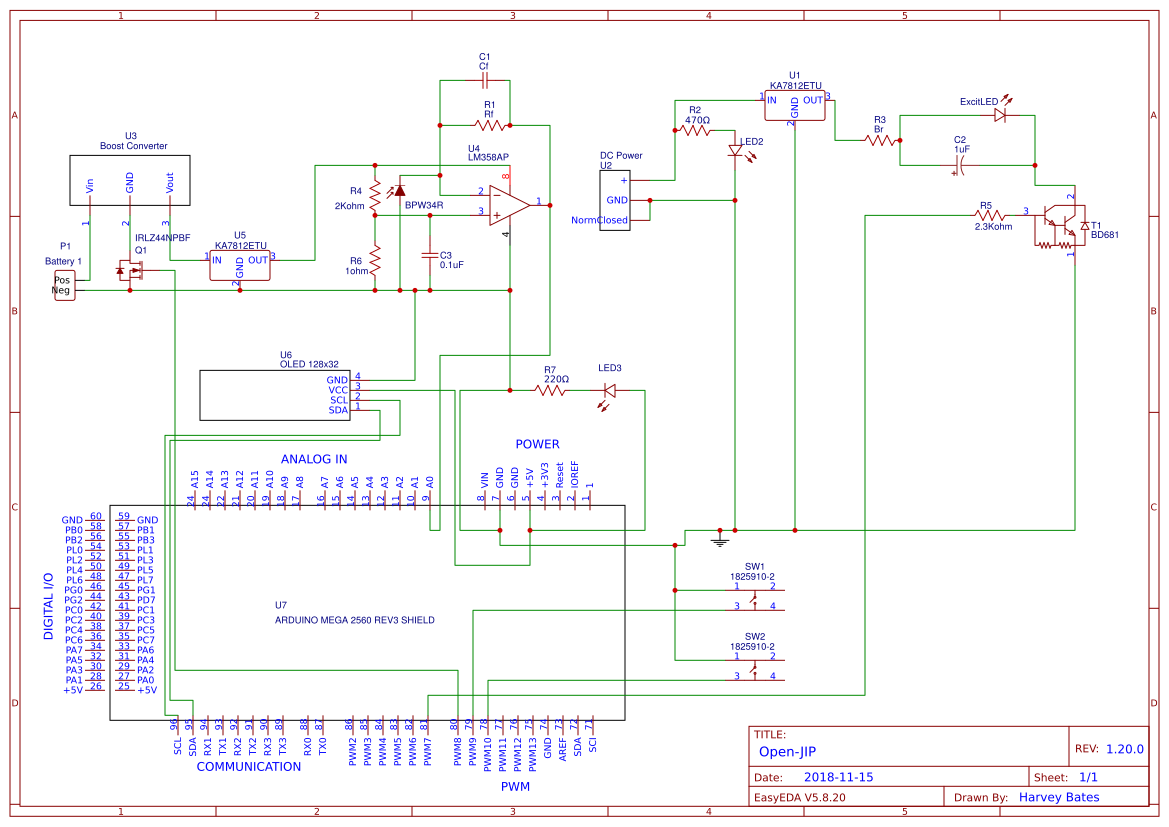
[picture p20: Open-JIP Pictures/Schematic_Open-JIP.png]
  
</p>

<p align="center">
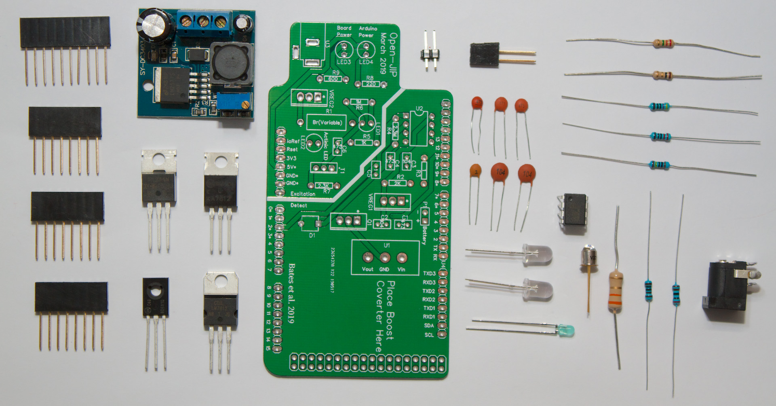
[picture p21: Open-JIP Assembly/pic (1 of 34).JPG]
  
</p>

The above image shows all the components needed to assemble the electronics of Open-JIP. You will also need some hookup wire (we use solid core wire, PRT-11367) a soldering iron, some solder and a pair of wire snips.

<p align="center">
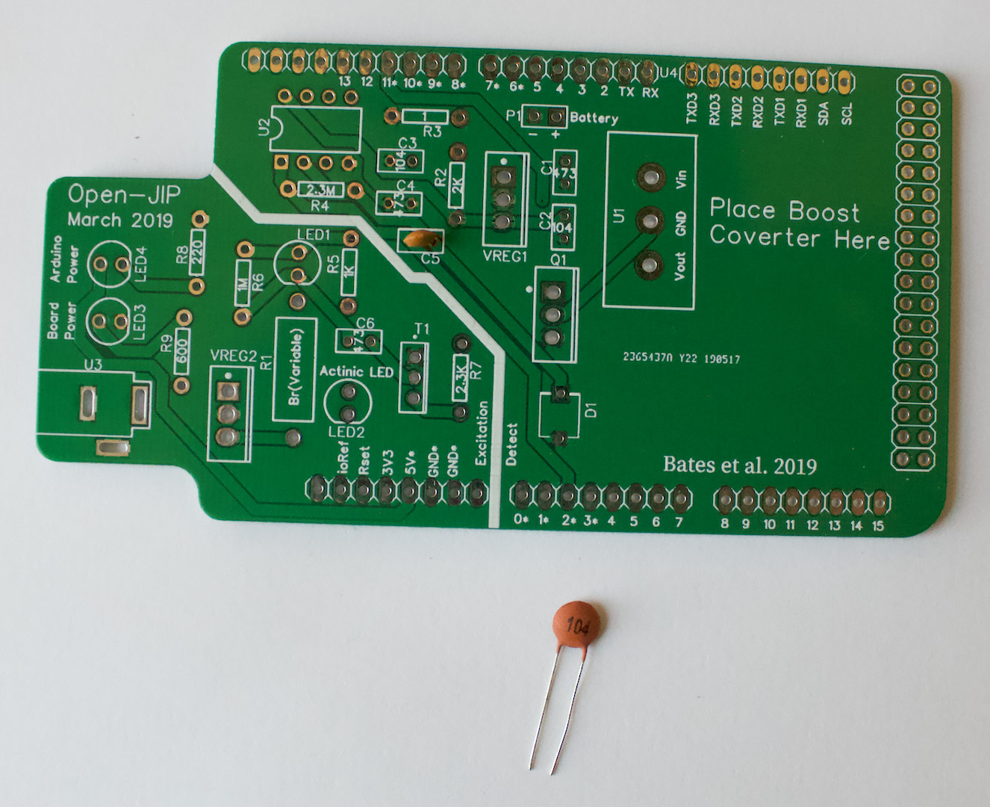
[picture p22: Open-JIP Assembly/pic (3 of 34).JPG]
  
</p>

Start with the small components, the capacitors and resistors. Look at the capacitors and you will see a code on the side (for this design we want 1, 473 and 104) this corosponds to a specific value of capacitance. On the printed circuit board (PCB) look for areas that match the code of capacitor and insert its legs into the holes. Orientation does not matter for these types of capacitors. On the opposite side of the PCB bend the legs of the capacitors to hold them in place. Continue this process until you have inserted all capacitors.

<p align="center">
  
</p>
<p align="center">
  
</p>

Once complete you want to solder the capacitors in place. To do this hold the soldering irons tip on the joint you want to solder for roughly two seconds and then add some solder, it should melt and envelop the joint and look like the photos below. 

<p align="center">
  
</p>
<p align="center">
  
</p>

Once you have soldered all capacitors then you can sip the trailing ends on the underside of the board as shown below.

<p align="center">
  
</p>

Follow the same process for all the resistors. Their specific resistance is marked on the PCB. Follow by adding the OP-AMP located in the top left corner of the below photo. Ensure the OP-AMPs orientation is correct by keeping the dot on the OP-AMP the same as in the photo below. 

<p align="center">
  
</p>

In the above photo you can see an LED which corrosponds to position on the PCB marked LED1. The anode is the shorter leg and goes on the flat side of the while marking on the PCB. 
Next up is the battery connector, this goes at position P1 with the short legs going into the PCB. 

<p align="center">
  
</p>

We will now place the two indicator LEDs' at the front of the board. The same as in the last LED keep the short leg on the flat edge of the markings on the PCB. 

<p align="center">
  
</p>

The next item is the photodiode preperation. We are using the solid core wire mentioned above and with the use of some solder we are going to attach the wire to the terminals of the photodiode. Black wire is used on the side with the extrusion on the photodiode and red for the other terminal. 

<p align="center">
  
</p>

We can use some bluetack here to hold the wire and LED in place.
<p align="center">
  
</p>

If the user wishes they may add some insulation around the solder joints to keep them from coming in contact.
Back to the board we want to add the attachement for plugging in the excitation LED. This is an offcut from the arduino header pins which you can cut off using your wire cutters as we only want two terminals. 

<p align="center">
  
</p>

The barrel connector for connecting the power supply is soldered next onto the front of the PCB.
<p align="center">
  
</p>

Next up we have the four large components the LM7812 voltage regulator, the IRL44ZN mosfet, the KA7812 voltage regulator and the BD681 darlington transitor. 

<p align="center">
  
</p>
<p align="center">
  
</p>
<p align="center">
  
</p>
<p align="center">
  
</p>

Now its time for the boost coverter. This goes over the lettering on the PCB that says "Place boost Converter Here". First we want to prepare the pins to get as good of a connection as possible. Do this by snipping away the underside solder joints of the boost coverter. BE SURE not to snip Vout, GND and Vin as we need these to be long to attach it to the board.

<p align="center">
  
</p>
<p align="center">
  
</p>

Place the boost coverter on the PCB with Vout, GND and Vin inserted into the corrosponding PCB holes. Use your soldering iron to heat up the solder joint as much as possible and use solder to create a strong connection.

<p align="center">
  
</p>

We will now attach the headers for the arduino mega. To do this insert the headers into the outside holes of the PCB. These line up perfectly with an Arduino Mega and will allow you to mount the circuit on the top of the board.

<p align="center">
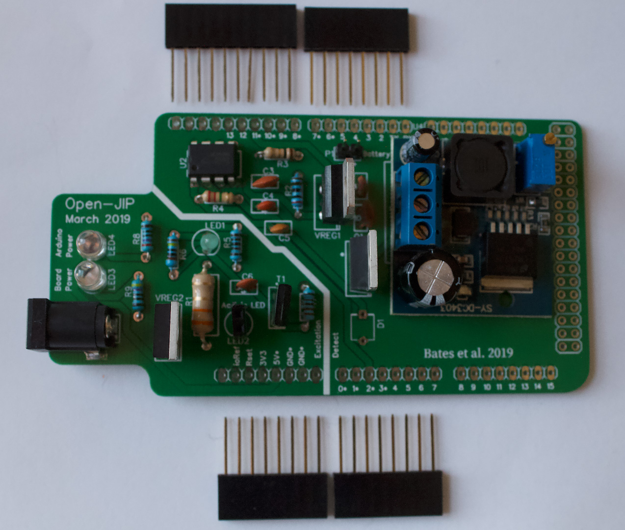
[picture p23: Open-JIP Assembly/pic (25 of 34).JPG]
  
</p>

Lastly measure the photodiode wires that we prepared above to be roughly ~105mm in length from the base of the photodiode to the inserts for the PCB. The red wire goes into the square solder mask on the PCB marked D1 and the black goes in the circular solder mask.

<p align="center">
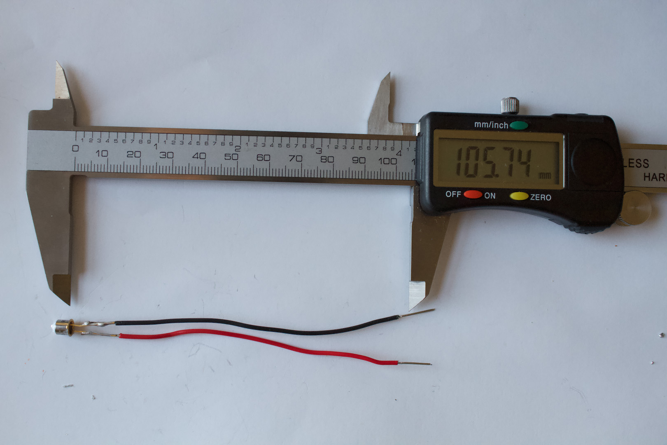
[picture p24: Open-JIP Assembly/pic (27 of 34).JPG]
  
</p>

You have now assembled Open-JIPs electronics circuit. 

# Construction of Open-JIP (Hardware)

<p align="center">
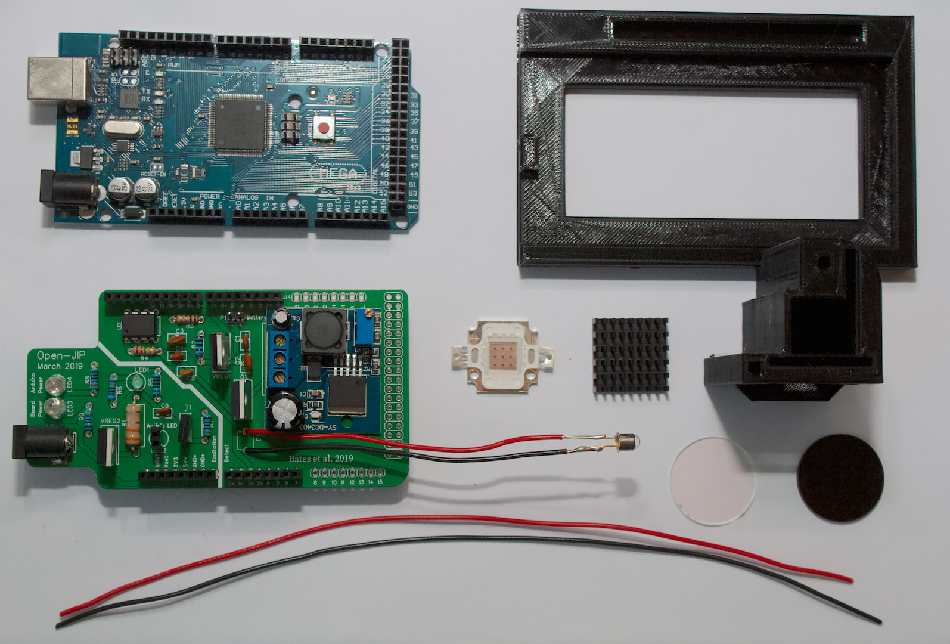
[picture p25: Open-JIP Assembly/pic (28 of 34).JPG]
  
</p>

For the hardware construction of Open-JIP we will need, the 3D printed scaffold, an arduino mega, the circuit board we just made, the 10W LED of choice (R, B, G, O), a heat sink for the LED (optional), a 695nm longpass filter and an IR-filter (as shown in the above image). You will also need some hookup wire (solid core), a soldering iron, some solder and some wire snips. To start off attach a decent length of hookup wire to the terminals of the LED with some solder, take note of the polarity of the LED when doing this.

<p align="center">
  
</p>

Next up attach the heatsink to the back of the LED. These usually have some thermal adheasive in which case you must peal off its cover before attaching. 

<p align="center">
  
</p>

Now its time to glue the LED to the 3D printed part, you can use any glue for this however I recommend 5 minute epoxy (not what is shown in the photo). 

<p align="center">
  
</p>
<p align="center">
  
</p>

Once cured we can attach the circuit board to the top of the Arduino and push it into its holder. Route and cut the wires from the LED though the holes and insert them into the spot on the PCB marked "Actinic LED". Push the photodiode into the small hole on the back side of the 3D printed structure it should be a tight fit. If not use a small amount of expoxy to secure it in place, ensuring that no expoxy gets on the face of the photodiode. 

<p align="center">
  
</p>

Lastly place the filters in the corrosponding spots. IR infront of the LED and 695nm longpass infront of the photodiode.

<p align="center">
  
</p>

You have now assembled Open-JIP Algae.

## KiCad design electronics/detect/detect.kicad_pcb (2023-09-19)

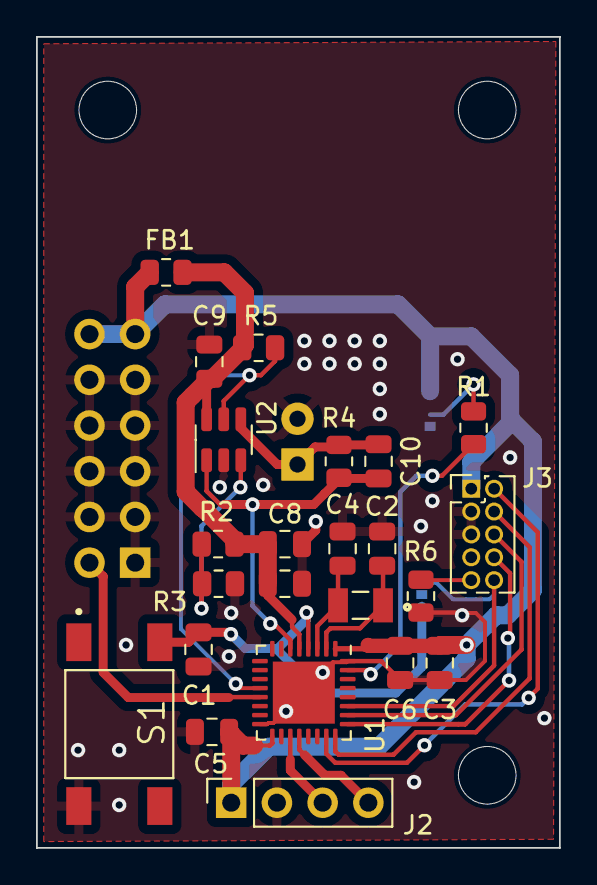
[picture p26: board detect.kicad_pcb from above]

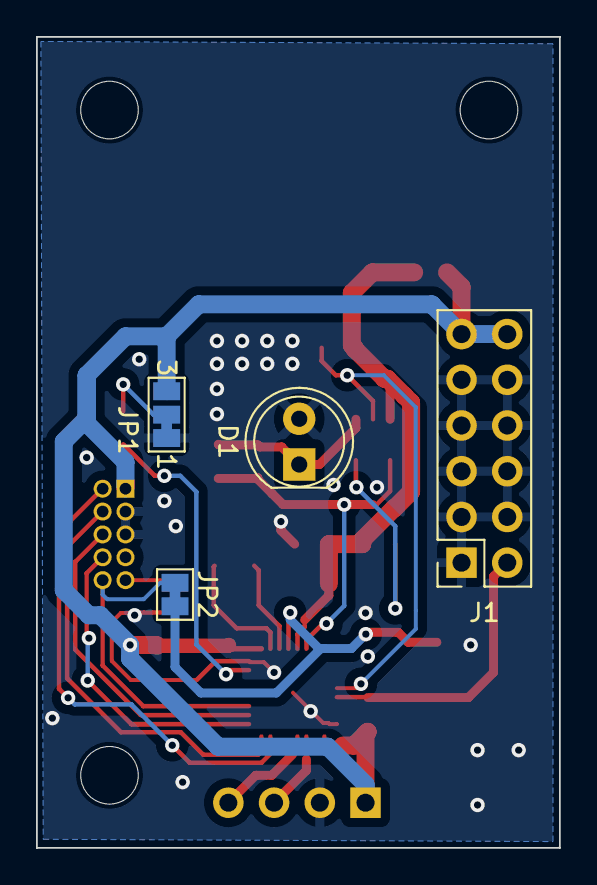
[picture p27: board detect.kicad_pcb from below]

Board: 2 copper layers, 29.1 x 45.1 mm, 27 parts (4 on the bottom side), 21 nets.

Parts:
C1, C3, C5, C9: 100nF; C_0805_2012Metric
C2, C4: 10pF; C_0805_2012Metric
C6: 4.7uF; C_0805_2012Metric
C7: 1uF; C_0805_2012Metric
C8: 10nF; C_0805_2012Metric
C10: 0.1pF; C_0805_2012Metric
D1: SFH213FA; LED_D5.0mm_IRGrey
FB1: R_0805_2012Metric
J1: Conn_02x06_Counter_Clockwise; PinSocket_2x06_P2.54mm_Vertical
J2: Conn_01x04_Socket; PinSocket_1x04_P2.54mm_Vertical
J3: Conn_ARM_JTAG_SWD_10; PinHeader_2x05_P1.27mm_Vertical
JP1: Boot_Sel; SolderJumper-3_P1.3mm_Bridged12_Pad1.0x1.5mm_NumberLabels
JP2: SolderJumper-2_P1.3mm_Bridged_Pad1.0x1.5mm
R1, R6: 10K; R_0805_2012Metric
R2: 1M; R_0805_2012Metric
R3: 33K; R_0805_2012Metric
R4: 500K; R_0805_2012Metric
R5: 100K; R_0805_2012Metric
S1: RESET; TL3301AF160QG
U1: STM32L432KCU6; QFN-32-1EP_5x5mm_P0.5mm_EP3.45x3.45mm
U2: OPA328DBVR; SOT-23-6
Y1: ECS-.327-12.5-34R-C-TR

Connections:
+3.3V: C3.1, C5.1, C6.1, FB1.2, J1.11, J1.12, J2.1, J3.1 (VTref), JP1.3 (B), U1.1 (VDD), U1.17 (VDD)
/ADC1_IN5: C10.2, R4.2, U1.6 (PA0), U2.1
/BOOT_SELECT: R1.2, U1.31 (PH3)
/PA6: R5.2, U1.12 (PA6), U2.5 (EN)
/PA7: J1.2, U1.13 (PA7)
/TCK/SWCLK_PA14: J3.4 (SWDCLK/TCK), U1.24 (PA14)
/TDI_PA15: J3.8 (NC/TDI), U1.25 (PA15)
/TDO/SWO_PB3: J3.6 (SWO/TDO), U1.26 (PB3)
/TMS/SWDAT_PA13: J3.2 (SWDIO/TMS), U1.23 (PA13)
/TRST_PB4: J3.10 (~RESET), JP2.1 (A), U1.27 (PB4)
/USART1_RX: J2.4, U1.20 (PA10)
/USART1_TX: J2.3, U1.19 (PA9)
GND: C1.2, C2.2, C3.2, C4.2, C5.2, C6.2, C7.2, C8.2, C9.2, D1.2 (A), J1.1, J1.3, J1.4, J1.5, J1.6, J1.7, J1.8, J1.9, J1.10, J2.2, J3.3 (GND), J3.5 (GND), JP1.1 (A), R3.2, R6.2, S1.2, U1.16 (VSS), U1.32 (VSS), U1.33 (VSS), U2.2 (V-)
NRST: C1.1, JP2.2 (B), S1.3, U1.4 (NRST)
unnamed: C10.1, D1.1 (K), R4.1, U2.4 (IN-)
unnamed: J3.9 (GNDDetect), R6.1
unnamed: JP1.2 (C), R1.1
unnamed: C2.1, U1.2 (PC14), Y1.1
unnamed: C4.1, U1.3 (PC15), Y1.2
unnamed: R2.2, R3.1, U2.3 (IN+)
VDDA: C7.1, C8.1, C9.1, FB1.1, R2.1, R5.1, U1.5 (VDDA), U2.6 (V+)

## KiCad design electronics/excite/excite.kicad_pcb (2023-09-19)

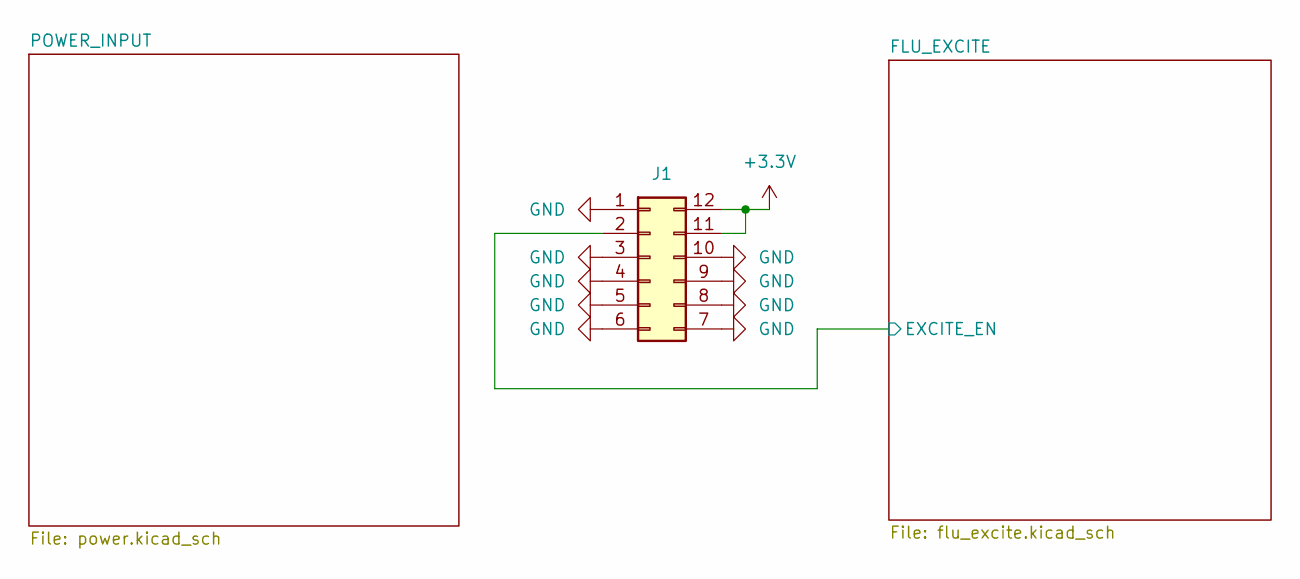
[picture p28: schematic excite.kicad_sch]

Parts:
J1: Conn_02x06_Counter_Clockwise; PinHeader_2x06_P2.54mm_Vertical

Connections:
+3.3V: J1.11, J1.12; also elsewhere on the board
/FLU_EXCITE/EXCITE_EN: J1.2; also elsewhere on the board
GND: J1.1, J1.3, J1.4, J1.5, J1.6, J1.7, J1.8, J1.9, J1.10; also elsewhere on the board

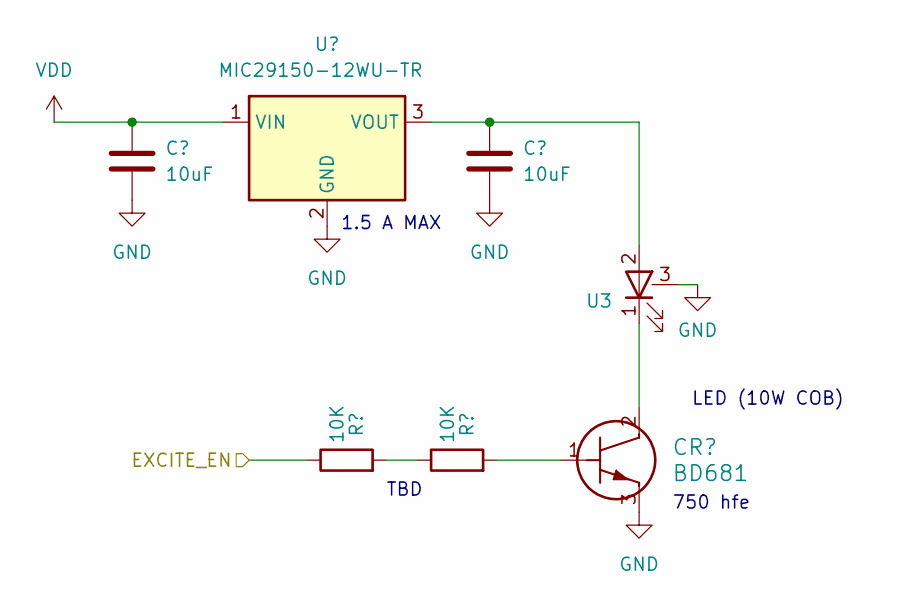
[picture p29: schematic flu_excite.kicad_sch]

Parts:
C5, C6: 10uF; CP_EIA-7343-15_Kemet-W; Part TAJD106K050RNJ
CR1: BD681
R2, R3: 10K; R_0805_2012Metric
U2: MIC29150-12WU-TR; MIC29150-12WU
U3: 10W_COB

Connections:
/FLU_EXCITE/EXCITE_EN: R2.1; also elsewhere on the board
GND: C5.2, C6.2, CR1.3, U2.2 (GND), U3.3; also elsewhere on the board
unnamed: CR1.1, R3.2
unnamed: CR1.2, U3.1
unnamed: R2.2, R3.1
unnamed: C6.1, U2.3 (VOUT), U3.2
VDD: C5.1, U2.1 (VIN); also elsewhere on the board

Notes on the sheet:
TBD
750 hfe
LED (10W COB)
1.5 A MAX

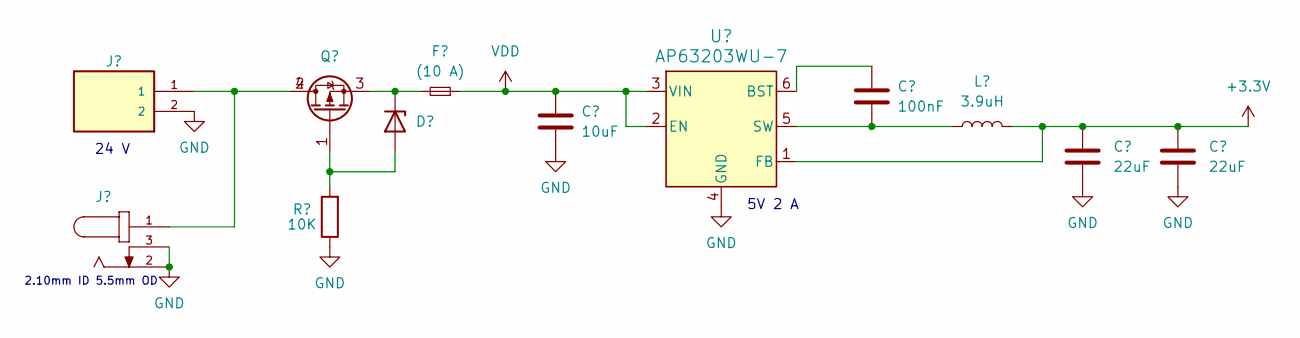
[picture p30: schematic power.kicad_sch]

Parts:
C1: 10uF; C_0805_2012Metric
C2: 100nF; C_0805_2012Metric
C3, C4: 22uF; C_0805_2012Metric
D1: D_Zener; MMSZ4700T1G
F1: (10 A); 0154010.DRL; Part 0154010.DRL
J2: TBP02R2-381-02BE
J3: PJ-002A
L1: 3.9uH; SDE0604A-3R9M; Part SDE0604A-3R9M
Q1: DMP6023LE-13
R1: 10K; R_0805_2012Metric
U1: AP63203WU-7; AP63205WU-7; Part AP63203WU-7

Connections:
+3.3V: C3.1, C4.1, L1.2, U1.1 (FB); also elsewhere on the board
GND: C1.2, C3.2, C4.2, J2.2, J3.2, J3.3, R1.1, U1.4 (GND); also elsewhere on the board
unnamed: D1.2 (A), Q1.1, R1.2
unnamed: D1.1 (K), F1.2, Q1.3
unnamed: J2.1, J3.1, Q1.2, Q1.4
unnamed: C2.1, U1.6 (BST)
unnamed: C2.2, L1.1, U1.5 (SW)
VDD: C1.1, F1.1, U1.2 (EN), U1.3 (VIN); also elsewhere on the board

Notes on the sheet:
24 V
5V 2 A
2.10mm ID 5.5mm OD

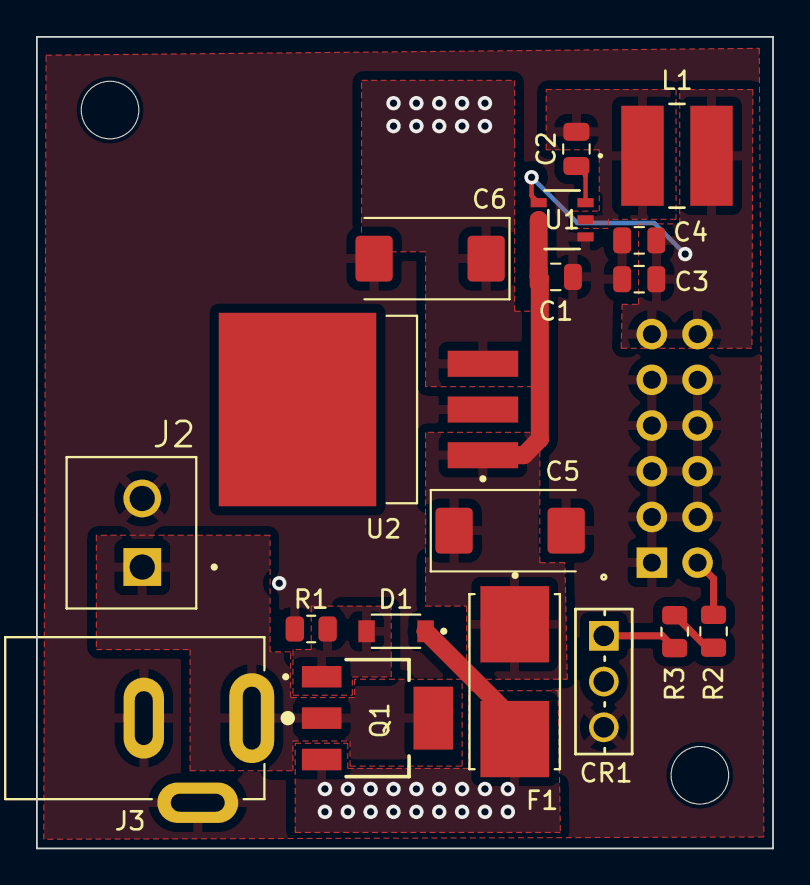
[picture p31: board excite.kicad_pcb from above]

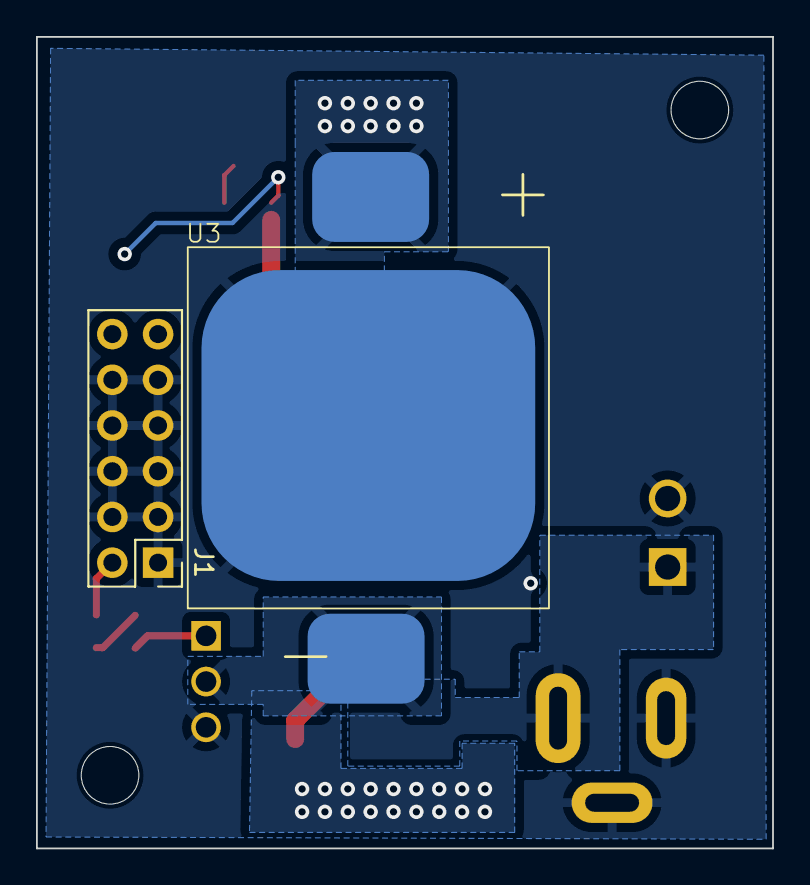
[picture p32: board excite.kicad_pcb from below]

Board: 2 copper layers, 40.9 x 45.1 mm, 20 parts (2 on the bottom side), 13 nets.

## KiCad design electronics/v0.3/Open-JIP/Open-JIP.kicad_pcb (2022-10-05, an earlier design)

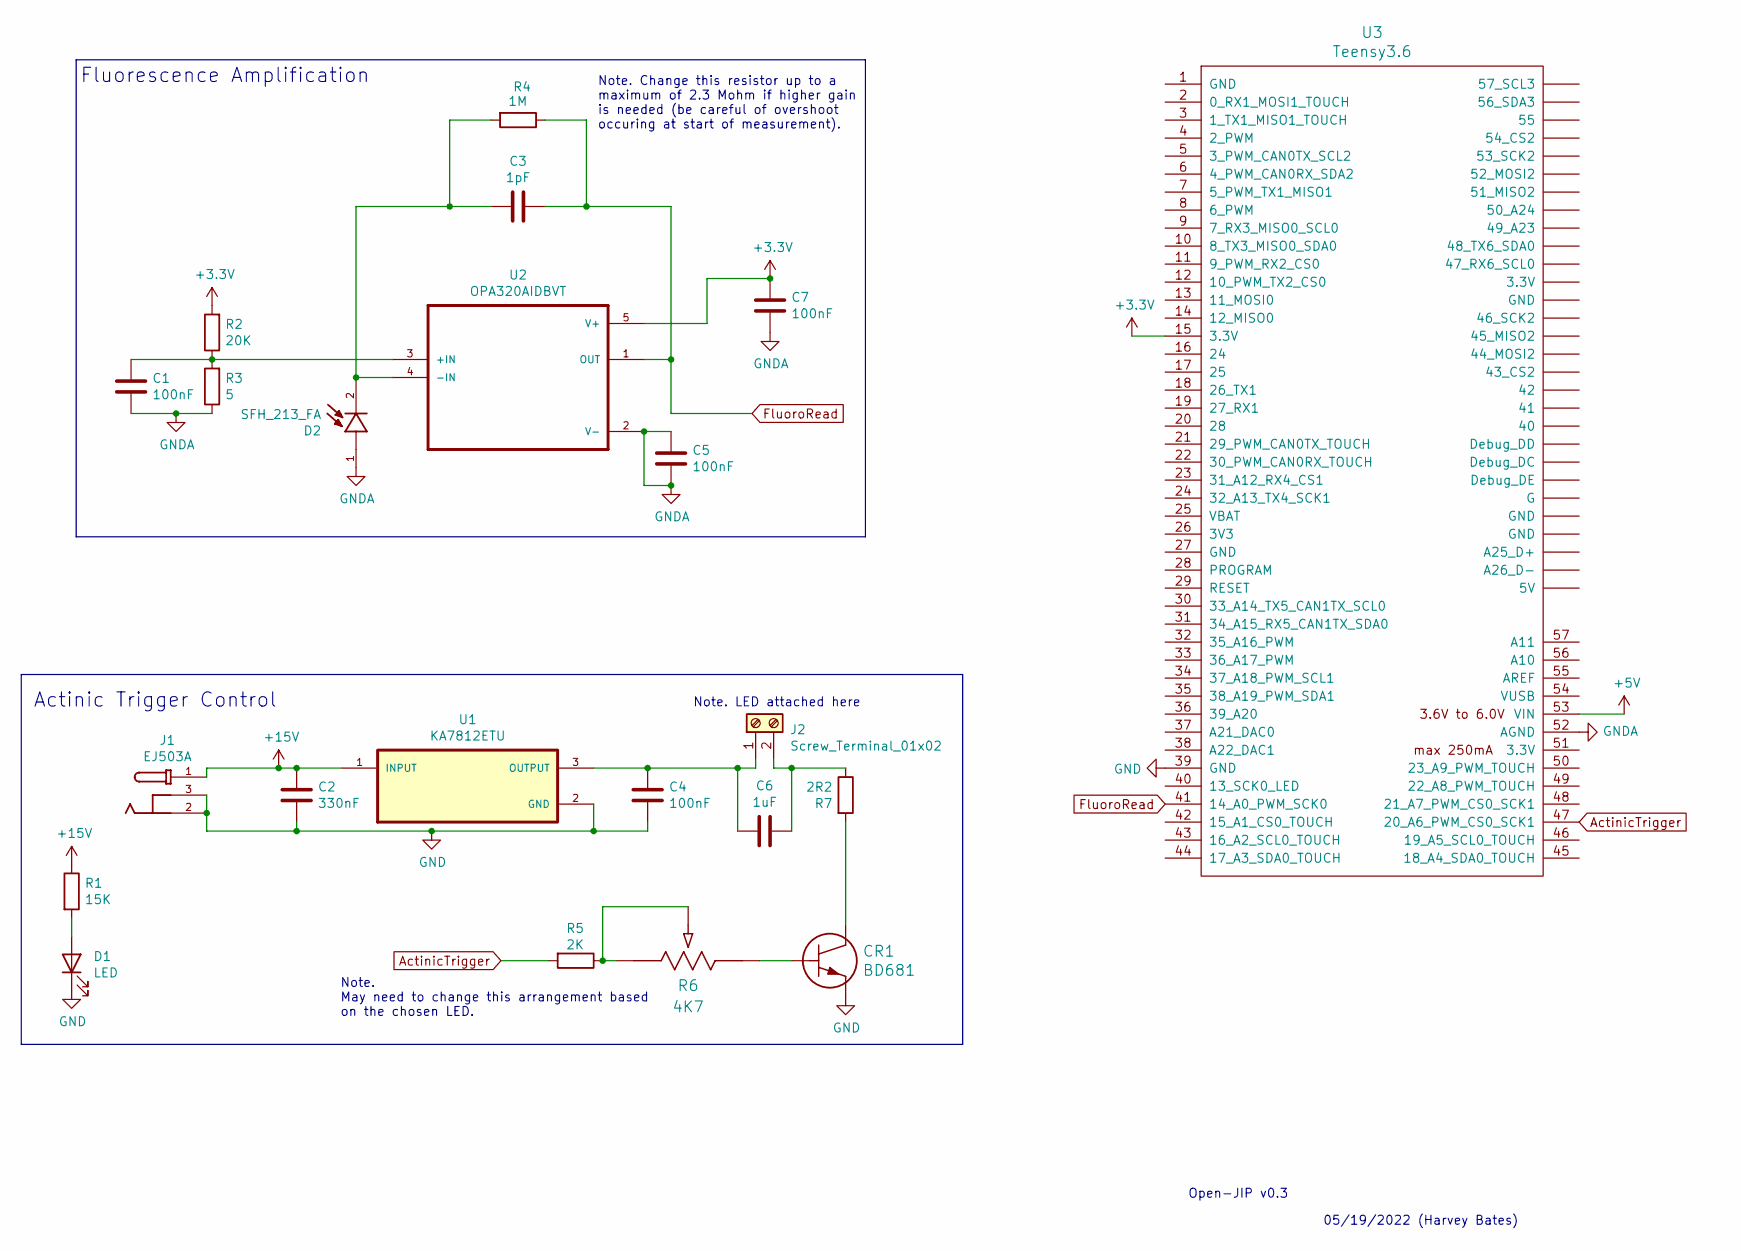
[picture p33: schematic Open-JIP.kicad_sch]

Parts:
C1, C4, C5, C7: 100nF; C_0805_2012Metric_Pad1.18x1.45mm_HandSolder
C2: 330nF; C_0805_2012Metric_Pad1.18x1.45mm_HandSolder
C3: 1pF; C_0805_2012Metric_Pad1.18x1.45mm_HandSolder
C6: 1uF; CP_Elec_4x5.4
CR1: BD681
D1: LED; LED_0805_2012Metric_Pad1.15x1.40mm_HandSolder
D2: SFH_213_FA; PARTREV 1.3
J1: EJ503A; PARTREV B
J2: Screw_Terminal_01x02; TerminalBlock_Altech_AK300-2_P5.00mm
R1: 15K; R_0805_2012Metric_Pad1.20x1.40mm_HandSolder
R2: 20K; R_0805_2012Metric_Pad1.20x1.40mm_HandSolder
R3: 5; R_0805_2012Metric_Pad1.20x1.40mm_HandSolder
R4: 1M; R_0805_2012Metric_Pad1.20x1.40mm_HandSolder
R5: 2K; R_0805_2012Metric_Pad1.20x1.40mm_HandSolder
R6: 4K7; 3386G-1-102LF
R7: 2R2; 35602R2JT
U1: KA7812ETU
U2: OPA320AIDBVT; OPA320AIDBVR
U3: Teensy3.6; Teensy35_36

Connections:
+3V3: C7.2, R2.2, U2.5 (V+), U3.15 (3.3V)
+5V: U3.53 (VIN)
+15V: C2.2, J1.1, R1.1, U1.1 (INPUT)
ActinicTrigger: R5.2, U3.47 (20_A6_PWM_CS0_SCK1)
FluoroRead: C3.1, R4.1, U2.1 (OUT), U3.41 (14_A0_PWM_SCK0)
GND: C2.1, C4.1, CR1.3 (E), D1.1 (K), J1.2, J1.3, U1.2 (GND), U3.39 (GND)
GNDA: C1.1, C5.1, C5.2, C7.1, D2.1, R3.1, U2.2 (V-), U3.52 (AGND)
unnamed: C1.2, R2.1, R3.2, U2.3 (+IN)
unnamed: C3.2, D2.2, R4.2, U2.4 (-IN)
unnamed: C4.2, C6.1, J2.1, U1.3 (OUTPUT)
unnamed: C6.2, J2.2, R7.1
unnamed: CR1.1 (B), R6.3
unnamed: CR1.2 (C), R7.2
unnamed: D1.2 (A), R1.2
unnamed: R5.1, R6.1, R6.2

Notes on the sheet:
Note. May need to change this arrangement based on the chosen LED.
05/19/2022 (Harvey Bates)
Fluorescence Amplification
Actinic Trigger Control
Open-JIP v0.3
Note. LED attached here
Note. Change this resistor up to a maximum of 2.3 Mohm if higher gain is needed (be careful of overshoot occuring at start of measurement).

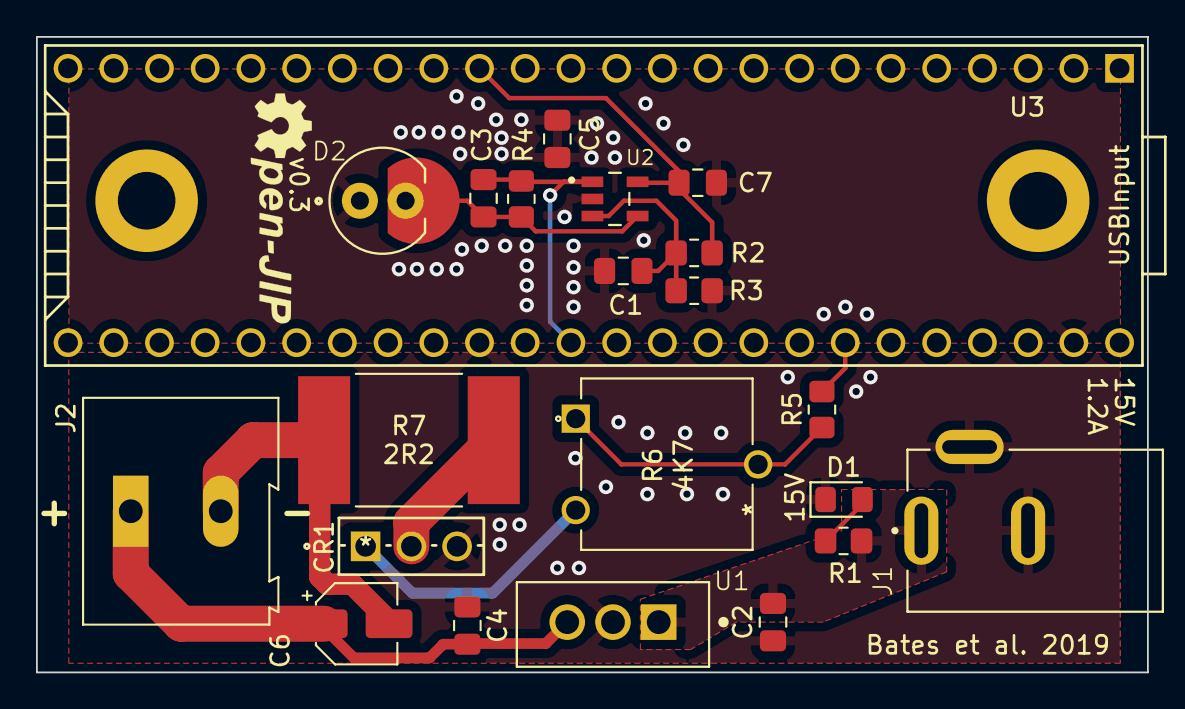
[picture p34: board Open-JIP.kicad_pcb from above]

Board: 2 copper layers, 61.7 x 35.3 mm, 22 parts (0 on the bottom side), 14 nets.

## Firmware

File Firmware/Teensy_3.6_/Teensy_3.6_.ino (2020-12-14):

/* <Open-JIP Teensy 3.6 Script. Controls "Open-JIP" chlorophyll fluorometer>
     Copyright (C) <2020>  <Harvey Bates>

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
     For more information contact: harvey.bates@student.uts.edu.au or see
     https://github.com/HarveyBates/Open-JIP 
*/ 

// Analog Pins
#define readPin 18

// Digital Pins
#define actinicPin 21

// Setup arrays that hold fluorescence data
int microRead [1000];
int milliRead[1000];

// Setup arrays that hold timestamps that correspond to fluorescence values
float microTime[1000]; 
float milliTime[1000];
String command;

int microLength = 1000, milliLength = 1000; // Change these to match the size of the above arrays

// Setup arrays to hold all datapoints and corresponding timestamps
float fluorescenceValues[2000];
float timeStamps[2000];

int fm = 0; // Initalise the fm value so we can calcualte it later

int fo_pos = 4; // Location of Fo in the measured array

float refVoltage = 3.3; // Set the reference voltage (only applicable with Teensy 3.6)

void setup() {
  Serial.begin(115200); // Initalise serial communications at specific baud rate
  analogReadResolution(12); // Set the resolution of the microcontroller in bits
  set_reference_voltage(refVoltage); // Only applicable with a Teensy 3.6 (disable if using other microcontroller)
  pinMode(actinicPin, OUTPUT); // Set the actinic pin as an output
  digitalWrite(actinicPin, LOW); // Make sure the actinic LED is turned off
  pinMode(13, OUTPUT); // Sets the microcontrollers LED pin as an output
}

void set_reference_voltage(float voltage){
  // Sets and initalises the required reference voltage for measurments
  if(voltage == 3.3){
    analogReference(DEFAULT); // Set to 3.3 V
  }
  else if(voltage == 1.1){
    analogReference(INTERNAL1V1); // Set to 1.1 V
  }
  else{
    analogReference(DEFAULT); // Set to default (3.3 V) if unknown value is found
  }
  analogRead(readPin); // Initalise reference voltage
}

void measure_fluorescence() {
//  set_reference_voltage(refVoltage); 
  
  digitalWrite(actinicPin, HIGH); // Turn on actinic LED

  long timer = micros(); // Start timer 

  // Read microsecond fluorescence values and corresponding timestamps
  for (unsigned int i = 0; i < sizeof(microRead) / sizeof(int); i++) 
  {
    microRead[i] = analogRead(readPin);
    microTime[i] = micros() - timer;
  }

  // Read millisecond fluorescence values and corresponding timestamps
  for (unsigned int i = 0; i < sizeof(milliRead) / sizeof(int); i++) 
  {
    milliRead[i] = analogRead(readPin);
    milliTime[i] = micros() - timer;
    delay(1);
  }
  
  digitalWrite(actinicPin, LOW); // Turn off actinic LED
  delay(10);

  // Convert micros() to milliseconds (ms) for microsecond values and convert bits to voltage
  for (unsigned int i = 0; i < sizeof(microRead) / sizeof(int); i++)
  {
   float milliReal = microTime[i]/1000; // Convert micros() to ms
   // Find fm value, we do this here while data are still ints
   if (microRead[i] > fm){
    fm = microRead[i];
   }
   fluorescenceValues[i] = (microRead[i] * refVoltage) / 4096; // Convert to volts and append to final array
   timeStamps[i] = milliReal; // Append time to final array
   Serial.print(milliReal, 3); 
   Serial.print("\t");
   Serial.println((microRead[i] * refVoltage) / 4096, 4);
   delay(1);
  }

  // Convert micros() to milliseconds for millsecond values and convert bits to voltage
  for (unsigned int i = 0; i < sizeof(milliRead) / sizeof(int); i++) 
  {
   float milliReal = milliTime[i]/1000; // Convert micros() to ms
   // Find fm value if not in microsecond range
   if (milliRead[i] > fm){
    fm = milliRead[i];
   }
   fluorescenceValues[i + microLength] = (milliRead[i] * refVoltage) / 4096; // Convert to V and append
   timeStamps[i + microLength] = milliReal; // Append to timestamps after microRead data
   Serial.print(milliReal, 3); 
   Serial.print("\t");
   Serial.println((milliRead[i] * refVoltage) / 4096, 4);
   delay(1);
  }
}

void calculate_parameters(){
  float fo = fluorescenceValues[fo_pos]; // Gets the minimum level fluorescence (Fo)
  float fj = 0.0f, fi = 0.0f;
  float  fj_time = 0.0f, fi_time = 0.0f, fm_time = 0.0f;
  bool fj_found = false, fi_found = false;

  // Next loop gets the Fj and Fi values at 2 and 30 ms respsctively 
  for(unsigned int i = 0; i < sizeof(timeStamps) / sizeof(int); i++){
    // Search for timestamp corresponding to 2 ms
    if(!fj_found && int(timeStamps[i]) == 2){
      fj = fluorescenceValues[i];
      fj_time = timeStamps[i];
      fj_found = true;
    }
    else if(!fi_found && int(timeStamps[i]) == 30){
      fi = fluorescenceValues[i];
      fi_time = timeStamps[i];
      fi_found = true;
    }
  }

  float fm_volts = (fm * refVoltage) / 4096.0;
  float fv = fm_volts - fo;
  float fvfm = fv / fm_volts;

  Serial.println();
  Serial.print("Fo: \t");
  Serial.print(fo, 4);
  Serial.print(" V @ ");
  Serial.print(timeStamps[fo_pos], 4);
  Serial.println(" ms");
  Serial.print("Fj: \t");
  Serial.print(fj, 4);
  Serial.println(" V @ " + String(fj_time) + " ms");
  Serial.print("Fi: \t");
  Serial.print(fi, 4);
  Serial.println(" V @ " + String(fi_time) + " ms");
  Serial.print("Fm: \t");
  Serial.print(fm_volts, 4);
  Serial.println(" V @ " + String(fm_time) + " ms");
  Serial.print("Fv: \t");
  Serial.print(fv, 4);
  Serial.println(" V");
  Serial.print("Quantum yield (Fv/Fm): \t");
  Serial.print(fvfm, 3);
  if(fvfm < 0.5){
    Serial.println(" Poor health");
  }
  else if(fvfm >= 0.5 && fvfm < 0.7){
    Serial.println(" Moderately healthy");
  }
  else if(fvfm >= 0.7){
    Serial.println(" Healthy");
  }
}

void calibrate_fo(){
  /* Calibrate the fo value of the fluorometer, can be used to ensure the concentration of algae
  is not too high
  */ 
  set_reference_voltage(refVoltage); 
  float foread = 0.0f;
  for (int k = 0; k < 5; k++){
    digitalWrite(actinicPin, HIGH);
    delayMicroseconds(20);
    for (int i = 0; i <= 2; i++){
      foread = analogRead(readPin);
      Serial.println((foread/4096) * refVoltage);
    }
    digitalWrite(actinicPin, LOW);
    Serial.print("Final Fo = ");
    Serial.println((foread/4096) * refVoltage);
    delay(2000);
    }
}

void calibrate_rise(){
  // Calibrate the rise time of the flurometer (useful for debugging)
  for (int i = 0; i < 200; i++){
    digitalWrite(actinicPin, HIGH);
    delayMicroseconds(100);
    digitalWrite(actinicPin, LOW);
    delay(200);
  }
}

void measure_light(){
  // Measure light using external 4pi light meter
  digitalWrite(actinicPin, HIGH);
  delay(3000);
  digitalWrite(actinicPin, LOW);
  delay(20);
}

void loop(){
  if(Serial.available()){   
    command = Serial.readStringUntil('\n');
    if(command.equals("MeasureFluorescence") || command.equals("MF")){
      measure_fluorescence();
    }
    else if(command.equals("CP")){
      calculate_parameters();
    }
    else if(command.equals("CFo")){
      calibrate_fo();
    }
    else if(command.equals("ML")){
      measure_light();
    }
    else if(command.equals("Cr")){
      calibrate_rise();
    }
    else{
      delay(100);
    }
  }
  digitalWrite(13, HIGH);
  delay(1000);
  digitalWrite(13, LOW);
  delay(1000);
}

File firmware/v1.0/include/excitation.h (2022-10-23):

#ifndef ACTINIC_H
#define ACTINIC_H

#include <Wire.h>
#include "detection.h"

class Excitation {
public:
    Excitation() = default;
    ~Excitation() = default;

    enum Brightness {
        LED_OFF = 0,
        LED_VERY_LOW = 80,
        LED_LOW = 100,
        LED_MEDIUM = 120,
        LED_HIGH = 140,
        LED_VERY_HIGH = 200,
        LED_MAX = 255,
    };

    static void setBrightness(Brightness brightness);
    static void begin();
    static void testRise(Brightness brightness, uint8_t n_rises,
                         uint16_t pulse_width);


private:
    static const byte DAC_ADDRESS = 0x4C;
};

#endif //ACTINIC_H

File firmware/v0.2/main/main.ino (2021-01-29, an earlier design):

/* <Open-JIP Teensy 3.6 Script. Controls "Open-JIP" chlorophyll fluorometer>
     Copyright (C) <2020>  <Harvey Bates>

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
     For more information contact: harvey.bates@student.uts.edu.au or see
     https://github.com/HarveyBates/Open-JIP 
*/ 

// Analog pin used to record the analog signal coming from the OP-amps output
#define readPin 18

// Digital pin used to trigger the actininc LED 
#define actinicPin 21

/* Setup for OJIP analysis 
 *  Length specifies the number of data points captured at two different 
 *  acquisition frequencies. 
 *  Microsecond (micro) = readings every 8 us
 *  Millisecond (milli) = readings every 1 ms
 *  
 *  Each value is stored with its corresponding timestamp. Thus, the length
 *  of each array must match their corresponding number of acquisitions. 
 *  E.g. microLength of 1000 means 1000 data points will be captured at 8 us 
 *  intervals, this must match the array size of microRead and microTime.
*/
int microLength = 1000;
int microRead[1000];
float microTime[1000]; 

int milliLength = 1000;
int milliRead[1000];
float milliTime[1000];

/* These arrays represent the final array size of OJIP fluorescence acquisitions.
 *  Thus they are calculated as:
 *  array size = microLength + milliLength
 *  
 *  They hold the full OJIP acquisition (time stamps and values) in volts
 *  and milliseconds.
 */
float fluorescenceValues[2000];
float timeStamps[2000];

/* Setup arrays for a single J-Step acquisitions.
 *  These are used to capture a single 2 ms rise from Fo to Fj.
 *  The same rules as noted above for the array size apply.
 *  E.g. Keep the array size of each component the same.
 *  
 *  Default: 250 acquisitions (2 ms) at 8 us per measurment
 */
unsigned int micorReadJLength = 250;
int microReadJ[250];
int microTimeJ[250];
float jValues[250];
float jTime[250];

/* Setup for the wave feature of J-step acquisitions (Multiple O-J rises). 
 * Large arrays are used to store consecutive O-J rises with (waveInterval) ms between  
 * measurments. 
 * 
 * Array sizes are calculated as follows:
 * array size = numWaves * waveAqu
 * 
 * Where waveAqu is the number of microsecond acquisitions used to resolve the
 * J-step and the number of waves represent your desired number of consecutive
 * O-J rises.
 */
unsigned int numWaves = 100; // Number of consecutive acquisitions
unsigned int waveInterval = 5; // Time between each O-J rise
unsigned int waveLength = 25000; // Array size of wave acquisitions
unsigned int waveAqu = 250; // Number of acquisitions in each O-J rise
int waveRead[25000];
int waveTime[25000];

int fm = 0; // Initalise the fm value so we can calcualte it later

int fo_pos = 4; // Location of Fo in the measured array

float refVoltage = 3.3; // Set the reference voltage (only applicable with Teensy 3.6)

String command; // Used for reading serial port requests

void setup() {
  Serial.begin(115200); // Initalise serial communications at specific baud rate
  analogReadResolution(12); // Set the resolution of the microcontroller in bits
  set_reference_voltage(refVoltage); // Only applicable with a Teensy 3.6 (disable if using other microcontroller)
  pinMode(actinicPin, OUTPUT); // Set the actinic pin as an output
  digitalWrite(actinicPin, LOW); // Make sure the actinic LED is turned off
  pinMode(13, OUTPUT); // Sets the microcontrollers LED pin as an output
}

void set_reference_voltage(float voltage){
  // Sets and initalises the required reference voltage for measurments
  if(voltage == 3.3){
    analogReference(DEFAULT); // Set to 3.3 V
  }
  else if(voltage == 1.1){
    analogReference(INTERNAL1V1); // Set to 1.1 V
  }
  else{
    analogReference(DEFAULT); // Set to default (3.3 V) if unknown value is found
  }
  analogRead(readPin); // Initalise reference voltage
}

void measure_j_step(){
  /* Measures up to the J-Step (2 ms) and prints the values in the serial output*/
  set_reference_voltage(refVoltage);
  digitalWrite(actinicPin, HIGH);
  long timer = micros();

  /* Read the values */
  for(unsigned int i = 0; i < sizeof(microReadJ) / sizeof(int); i++){
    microReadJ[i] = analogRead(readPin);
    microTimeJ[i] = micros() - timer;
  }

  digitalWrite(actinicPin, LOW);

  /* Convert and print out the values */
  for(unsigned int i = 0; i < sizeof(microReadJ) / sizeof(int); i++){
    jTime[i] = microTimeJ[i] / 1000.0; // Convert to ms
    jValues[i] = (microReadJ[i] * refVoltage) / 4096.0; // Convert bits to V
    Serial.print(jTime[i], 3); 
    Serial.print("\t");
    Serial.println(jValues[i], 4);
    delay(5);
  }
}


void wave(){
  set_reference_voltage(refVoltage); 
  int wavePos = 0; // Keeps track of position in wave acquisition array
  for(unsigned int i = 0; i < numWaves; i++){
    
    digitalWrite(actinicPin, HIGH);
    long timer = micros();
      
    for(unsigned int x = 0; x < waveAqu; x++){
      waveRead[wavePos] = analogRead(readPin);
      waveTime[wavePos] = micros() - timer;
      wavePos++;
    }
    
    digitalWrite(actinicPin, LOW);
    delay(waveInterval); // Delay for specified interval
  }

  // Prints out the data
  for(unsigned int i = 0; i < waveLength; i++){
    Serial.print(waveTime[i] / 1000.0, 3); 
    Serial.print("\t");
    Serial.println((waveRead[i] * refVoltage) / 4096.0, 4);
  }
}
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

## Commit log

2019-05-17 PCB Open_JIP Gerber
2019-07-19 Add files via upload
    Bill of Materials for Open-JIP
    [BOM_Open-JIP.xlsx]
2019-07-19 Open-JIP Models
    [Open-JIP Algae v2.f3d, Open-JIP Algae v2.stl, Open-JIP Plant Aperture v1.f3d, Open-JIP Plant Aperture v1.stl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]
2020-09-09 major update
    [BOM_Open-JIP.xlsx]
2020-11-14 updates for new version (v0.2)
    [BOM_Open-JIP.xlsx, Cuvette Housing.stl, LED Cover.stl, Open-JIP Algae v2.f3d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]
2020-11-15 update BOM
    [BOM.csv, Phenobottle v18.csv]
2020-11-15 added pcb ordering info
    [Phenobottle v18-NPTH.drl, Phenobottle v18-PTH.drl]
2020-11-22 changed CB from pdf to gbr
    [Phenobottle v18-B_Cu.gbr, Phenobottle v18-B_Mask.gbr, Phenobottle v18-B_Paste.gbr, Phenobottle v18-B_SilkS.gbr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]
2020-11-22 changed silkscreen
    [Phenobottle v18-B_Cu.gbr, Phenobottle v18-B_Mask.gbr, Phenobottle v18-B_Paste.gbr, Phenobottle v18-B_SilkS.gbr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]
2020-12-08 upgraded BOM and 3d-models
    [BOM.csv, Cuvette Housing.stl, LED Cover.stl, LEDCover.stl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]
2020-12-11 started on v0.3
    [74HC4066D_653.step, 826634-5--3DModel-STEP-1.STEP, AOD417.step, B2B-PH-K-S(LF)(SN)--3DModel-STEP-56544.STEP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]
2020-12-15 resiszed to fit quartz cuvette
    [MainFrame.stl, Open-JIPAlgae(DesktopVersion).f3z, Open-JIPAlgae(DesktopVersion).step]
2020-12-17 restructure and add teensy 4.1 support
2020-12-19 working on CSV to plot
    [Open-JIP_Data.csv]
2020-12-20 added plotting capability using plotly
    [Open-JIP_Data.csv]
2020-12-25 added adjustable gain for teensy 3.6
    [74HC4066D_653.step, 826634-5--3DModel-STEP-1.STEP, AOD417.step, B2B-PH-K-S(LF)(SN)--3DModel-STEP-56544.STEP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]
2020-12-25 started designing board for teensy 3.6
    [Open-JIP(KiCad)_T3.6.sch]
2020-12-26 finalised v0.3 for teensy 3.6
    [DCJack_EJ503A.step, Open-JIP(KiCad)_T3.6.kicad_pcb, Open-JIP(KiCad)_T3.6.sch]
2020-12-26 started on v0.3 for teensy 3.2
    [Open-JIP(KiCad).kicad_pcb, Open-JIP(KiCad).sch, Open-JIP(KiCad)_T3.2.sch, Open-JIP(KiCad)_T3.6.kicad_pcb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]
2020-12-26 added v0.3 for teensy 3.1-2-LC
    [Open-JIP(KiCad)_T3.2.kicad_pcb]
2020-12-26 finished v0.3 for teensy 3.2 and added gerber files
    [Open-JIP(KiCad).kicad_pcb, Open-JIP(KiCad).sch, Open-JIP(KiCad)_T3.2-B_Cu.gbr, Open-JIP(KiCad)_T3.2-B_Mask.gbr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]
2021-01-27 added J-step measuring procedure
    [Open-JIP(KiCad)_T3.6-B_Cu.gbr, Open-JIP(KiCad)_T3.6-B_Mask.gbr, Open-JIP(KiCad)_T3.6-B_Paste.gbr, Open-JIP(KiCad)_T3.6-B_SilkS.gbr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]
2021-01-27 adjusted wave to output volts and ms
2021-02-01 update firmware for v0.3
    [Open-JIP(KiCad)_T3.6.sch]
2021-02-10 update cntrl and firmware for v0.3
    [Open-JIP_Data.csv]
2021-02-16 update external cntrl
    [Open-JIP_Data.csv]
2021-03-02 changed how the actinic LED is triggered
2021-03-05 adding optical density to fluorometer
    [FDN337N.step, Open-JIP(KiCad)_T3.6.sch, VREG_L7805ACD2T.step]
2021-03-07 od and fluorometer design
    [B3B-PH-SM4-TB_LF__SN_.step, Open-JIP(KiCad)_T3.6-B_Cu.gbr, Open-JIP(KiCad)_T3.6-B_Mask.gbr, Open-JIP(KiCad)_T3.6-B_Paste.gbr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]
2021-03-11 refactored electronics desgin
    [Infineon_PG-LLGA-5-1.FCStd, L_Coilcraft_LPS5030.FCStd, L_Wuerth_WE-TPC-3816.FCStd, Open-JIP(KiCad)_T3.6-B_Cu.gbr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]
2021-07-10 updating structure and documentation
    [74HC4066D_653.step, 826634-5--3DModel-STEP-1.STEP, AOD417.step, B2B-PH-K-S(LF)(SN)--3DModel-STEP-56544.STEP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]
2021-07-14 updated v0.3 bom
    [BOM.csv, Open-JIP(KiCad)_T3.6.kicad_pcb]
2022-09-03 working on v1.0
    [74HC4066D_653.step, AOD417.step, B3B-PH-SM4-TB_LF__SN_.step, BOM.csv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]
2022-09-12 added precision current source for excitation LED
    [S2B-PH-SM4-TB_LF__SN_.step, open_jip.kicad_sch]
2022-09-19 finalised prototype components and started on PCB
    [2SD2671TL.step, XPEBRD-L1-0000-00901.step, open_jip.kicad_sch]
2022-10-05 updated file structure of project
    [826634-5--3DModel-STEP-1.STEP, AOD417.step, B2B-PH-K-S(LF)(SN)--3DModel-STEP-56544.STEP, B3B-PH-SM4-TB_LF__SN_.step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]
2022-10-05 further updates to file structure
    [2SD2671TL.step, 74HC4066D_653.step, AOD417.step, CONUFL001-SMD-T.step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]
2022-10-05 rename file structure for v0.3
    [EJ503A.step, KA7812ETU.step, OPA320AIDBVR.step, SFH_213_FA.step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]
2022-10-12 added some prelim firmware for v1.0, updated schematic and pcb to remove the second stage trans impedance amplifier on both detection excitation
    [open_jip.kicad_sch]
2022-10-13 sent of two versions to be manufactured, one smd photodiode other with tht
    [SFH_213_FA.step, open_jip-B_Cu.gbr, open_jip-B_Mask.gbr, open_jip-B_Paste.gbr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]
2022-10-23 updates to version 1.0 with 18650 and new power supply
    [1043.step, 1048P--3DModel-STEP-56544.step, open_jip.kicad_sch]
2023-09-05 update for next round of hardware testing
    [0154010.DRL.step, 0ZCF0075AF2C.step, 0ZCF0100AF2A.step, 1043.step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]
2023-09-07 updating PCB layout
    [flu_detect.kicad_sch, open-jip.kicad_pcb, power.kicad_sch]
2023-09-17 updated with two PCB's one detect, one excite, need to route the excite board and move the LED inline with cuvette
    [0154010.DRL.step, 0ZCF0075AF2C.step, 0ZCF0100AF2A.step, 10W LED.STEP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]
2023-09-19 working on cuvette mount and finished routing both pcbs
    [detect.kicad_pcb, excite.kicad_pcb, open_jip.FCStd]

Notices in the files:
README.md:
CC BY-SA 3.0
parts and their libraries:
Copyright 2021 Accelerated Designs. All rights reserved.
